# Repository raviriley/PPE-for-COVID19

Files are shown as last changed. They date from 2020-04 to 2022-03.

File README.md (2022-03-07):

Featured on Dr. Neat's Vlog: https://www.youtube.com/watch?v=sHTiJ7Pke1Q

---

##### PPE Makers/Assemblers: [Ravi Riley](https://github.com/raviriley), [Sako Chekerjian](https://github.com/sakorocco), Eric Limonadi, [Adam Komjathy](https://github.com/adamkomjathy)

##### Donors: [FRC Team 589](https://cvrobots.com), my parents, [Dr. Neat](http://www.drneato.com)

##### Recipients: Verdugo Hills Hosptial, Keck Medicine of USC, CVHS, local essential workers

 

---

We need help fabricating face shields and surgical mask strain relievers.

### **Take Action**

Each face shield consists of just 2 parts: a 3D-printed frame and a transparent visor. For more info on the design, click [here](https://3dverkstan.se/protective-visor/).

<div>
<a href="https://mk03dverkstanb4pk6hu.kinstacdn.com/wp-content/uploads/2020/04/liggande1.jpg">

</a>
<a href="https://mk03dverkstanb4pk6hu.kinstacdn.com/wp-content/uploads/2020/04/printoh3.jpg">

</a>
</div>

If you have a 3D printer, print [face shield frames (stl)](https://github.com/raviriley/PPE-for-COVID19/blob/master/Face%20Shield/Face%20Shield%20Frame.stl) and [surgical mask strain relievers (stl)](/surgical%20mask%20strap%20strain%20relief.stl). Ideally print with PETG, if you can't PLA works just as well.
Read this [print guide](https://3dverkstan.se/protective-visor/protective-visor-print-guide/) for more details.

Printing face shield frames one at a time can be super time consuming, so if you want to 3D print stacks of face shields, check out my stack generator on [Thingiverse Customizer](https://www.thingiverse.com/apps/customizer/run?thing_id=4311414) or run its [OpenSCAD script](https://github.com/raviriley/PPE-for-COVID19/tree/master/Face%20Shield/3D%20Printing%20Stacks/Customizable%20stack%20generator) locally. I built this tool using my [STL to OpenSCAD converter](https://github.com/raviriley/STL-to-OpenSCAD-Converter). Scroll down to see a demo of the stack generator script.

If you have a laser cutter, cut [face shield visors](/Face%20Shield/Templates%20%26%20Laser%20Cutting%20files) from transparent 8.5x11" sheets, such as [this](https://www.amazon.com/CFS-Products-Inches-Binding-Covers/dp/B07SB6ZKBD) or [this](https://www.amazon.com/Fellowes-Binding-Presentation-Covers-52089/dp/B0015ZVXIW/).

If you want to help out, please 
so we can buy more filament and plastic sheets. Thank you to our current donors for their contributions!

---

### COVID-19 Information/Trackers

- [CDC - How to make a cloth face mask](https://www.cdc.gov/coronavirus/2019-ncov/prevent-getting-sick/diy-cloth-face-coverings.html)

- [Johns Hopkins Interactive Map](https://coronavirus.jhu.edu/map.html)

- [Google Mobility Trends](https://www.google.com/covid19/mobility/)

---

**Explore more 3D printable designs at the [National Institutes of Health 3D Print Exchange for COVID-19](https://3dprint.nih.gov/collections/covid-19-response)**

---

#### Demo of Face Shield Stacker OpenSCAD Script

Demo of OpenSCAD Script

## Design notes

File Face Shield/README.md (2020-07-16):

To get started, print out a [`0.5in spacer.stl`](https://github.com/raviriley/PPE-for-COVID19/blob/master/Face%20Shield/0.5in%20spacer.stl) for your holepuncher. If you'll be printing face shield frames one at a time, download [`Face Shield Frame.stl`](https://github.com/raviriley/PPE-for-COVID19/blob/master/Face%20Shield/Face%20Shield%20Frame.stl). If you want to print stacks of face shields, explore the stacks folder or click [here](https://www.thingiverse.com/apps/customizer/run?thing_id=4311414) to generate your own custom stacks on Thingiverse Customizer. If you have OpenSCAD, download [`run locally.zip`](https://github.com/raviriley/PPE-for-COVID19/raw/master/Face%20Shield/3D%20Printing%20Stacks/Customizable%20stack%20generator%20(for%20single%20extrusion)/run%20locally.zip) to generate your own custom stacks locally. I suggest rendering locally, as it'll be a lot faster than using Thingiverse Customizer since these are quite large files. 
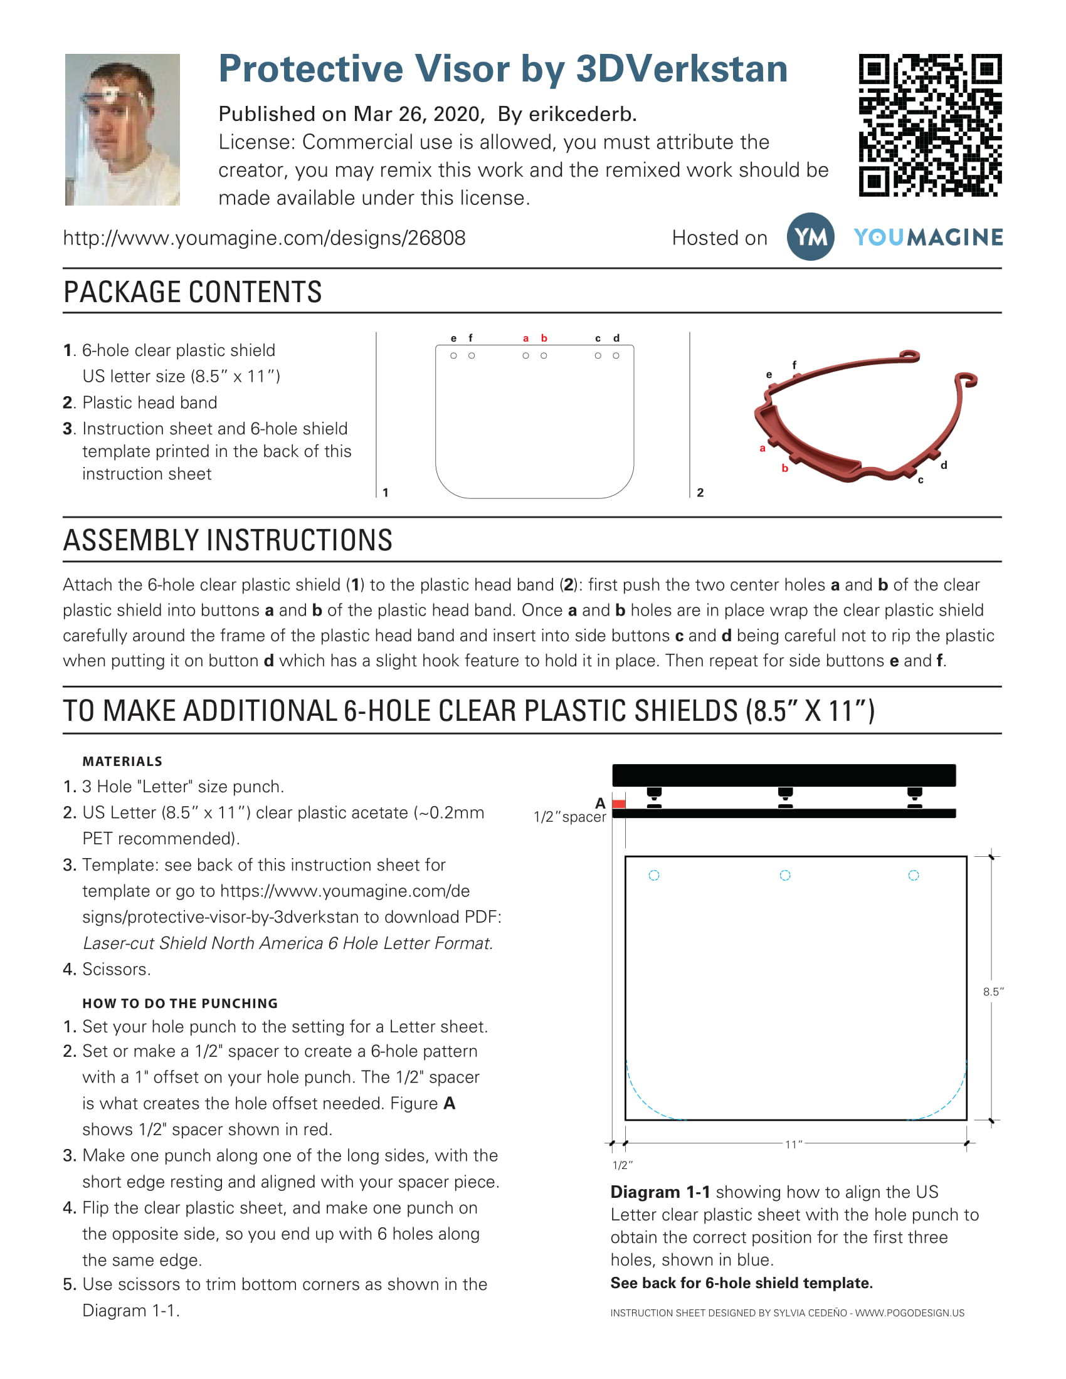
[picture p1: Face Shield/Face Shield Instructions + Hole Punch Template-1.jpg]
Face Shield Instructions and Hole Punch Template Page 1

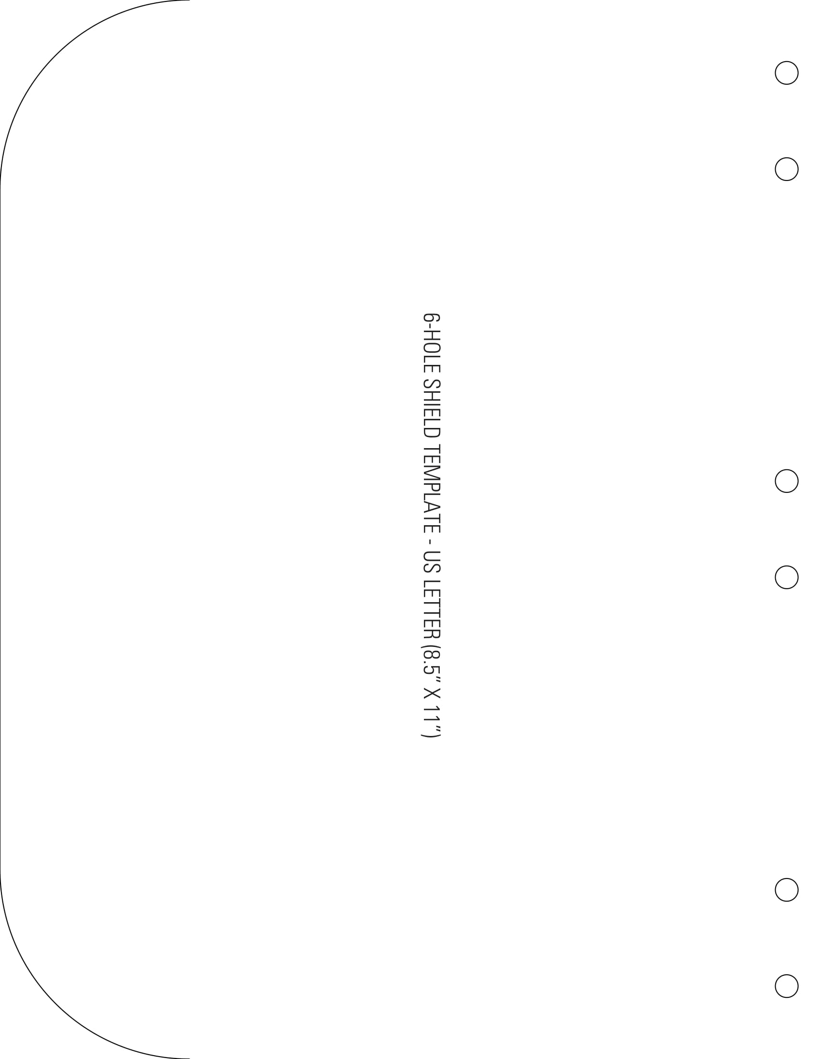
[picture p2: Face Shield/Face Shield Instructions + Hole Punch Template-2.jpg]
Face Shield Instructions and Hole Punch Template Page 2


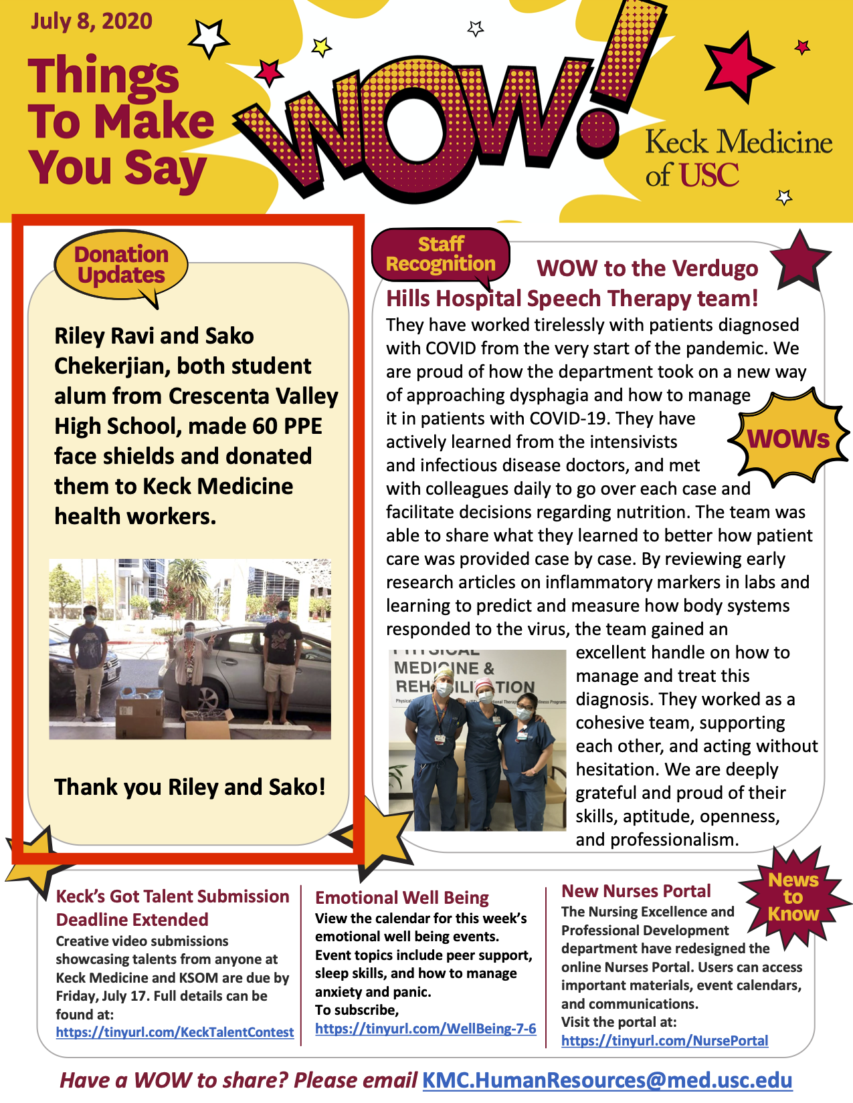
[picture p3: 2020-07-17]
images/USC-newsletter.png

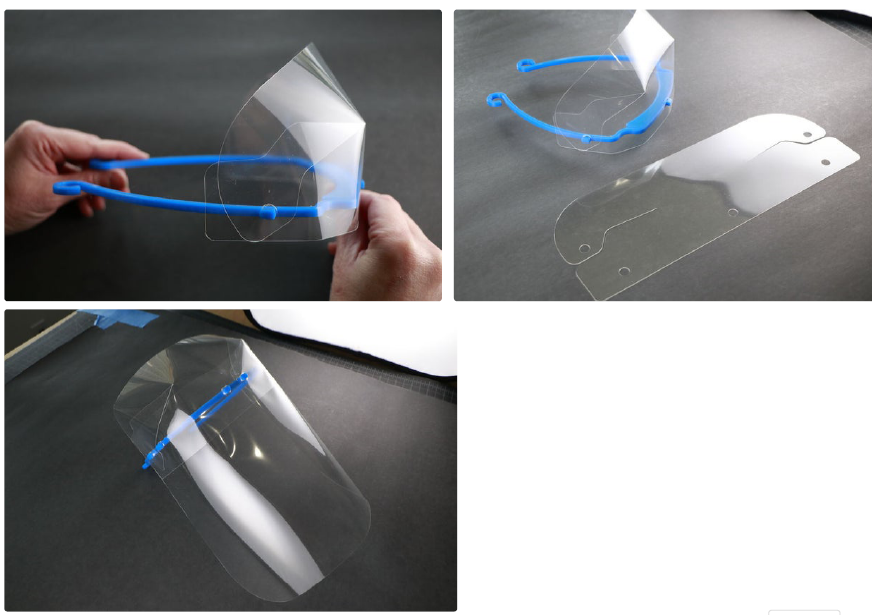
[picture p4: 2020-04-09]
Face Shield/Templates & Laser Cutting files/Top Covers/Capture.PNG

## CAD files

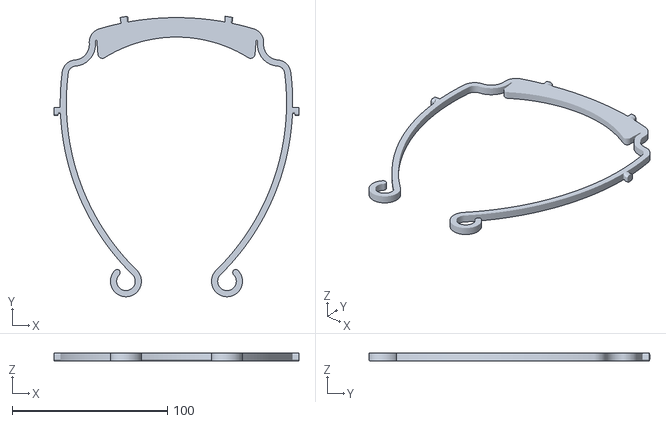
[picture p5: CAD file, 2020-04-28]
Face Shield/3D Printing Stacks/Customizable stack generator/Europe ISO838_v4-solid_front.stl
158.0 x 181.0 x 5.00

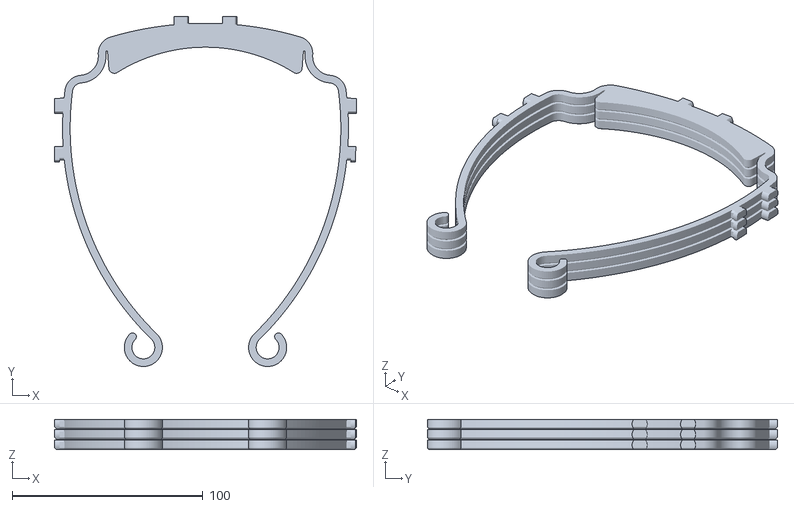
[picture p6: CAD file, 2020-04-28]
Face Shield/3D Printing Stacks/stack of 3 - 16mm tall.stl
158.5 x 183.6 x 16.0

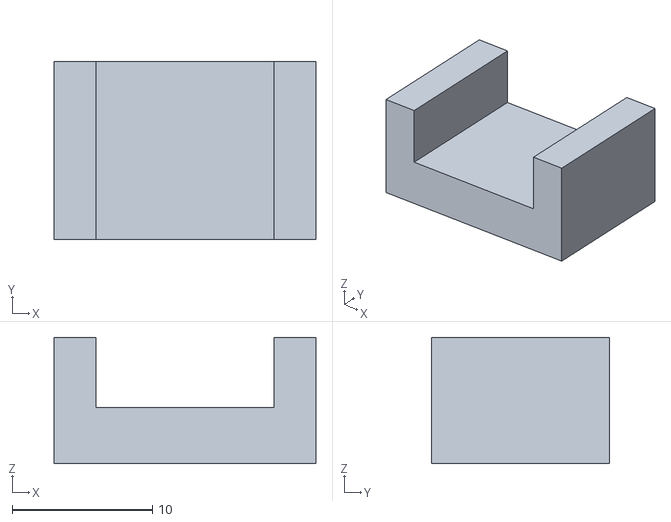
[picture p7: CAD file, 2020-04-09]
Face Shield/all US frame variants/Letter-spacer-6hole.stl
18.7 x 12.7 x 9.00

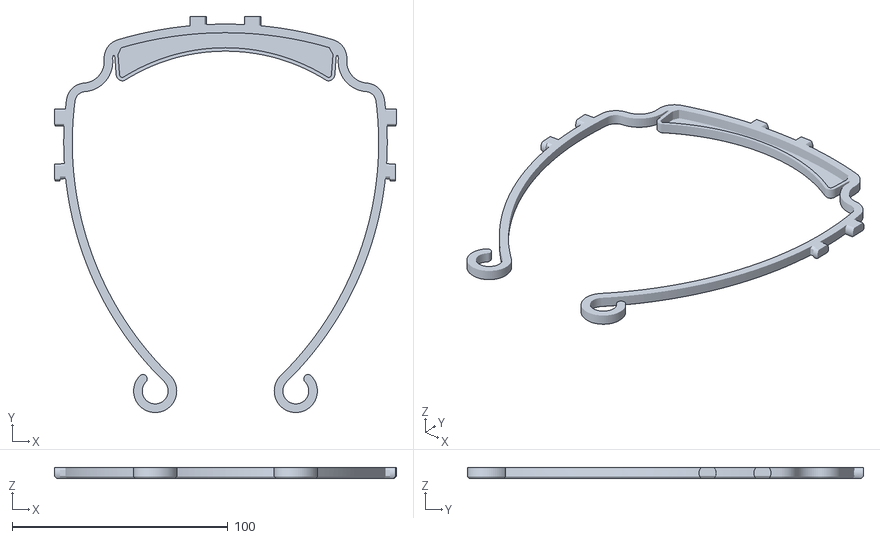
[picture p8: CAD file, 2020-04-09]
Face Shield/Face Shield Frame.stl
158.5 x 183.6 x 5.00

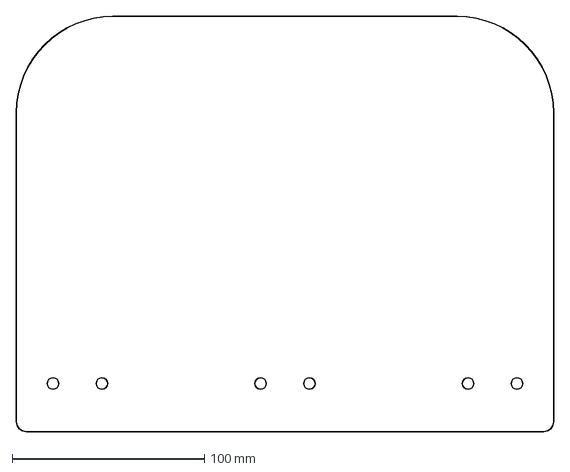
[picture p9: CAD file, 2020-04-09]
Face Shield/Templates & Laser Cutting files/US 6 Hole Template by Joel Telling.dxf
279.4 x 215.9 mm

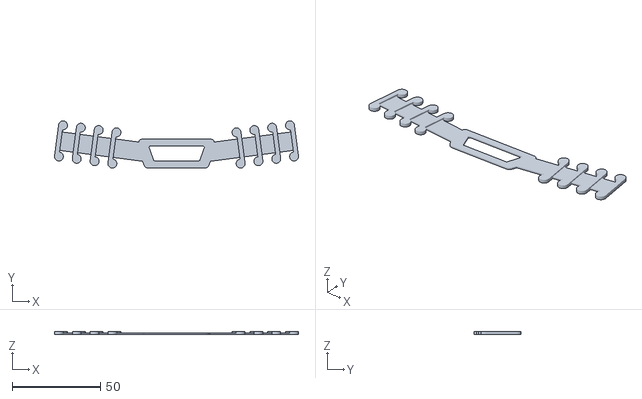
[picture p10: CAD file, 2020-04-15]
surgical mask strap strain relief.stl
138.5 x 26.8 x 1.70

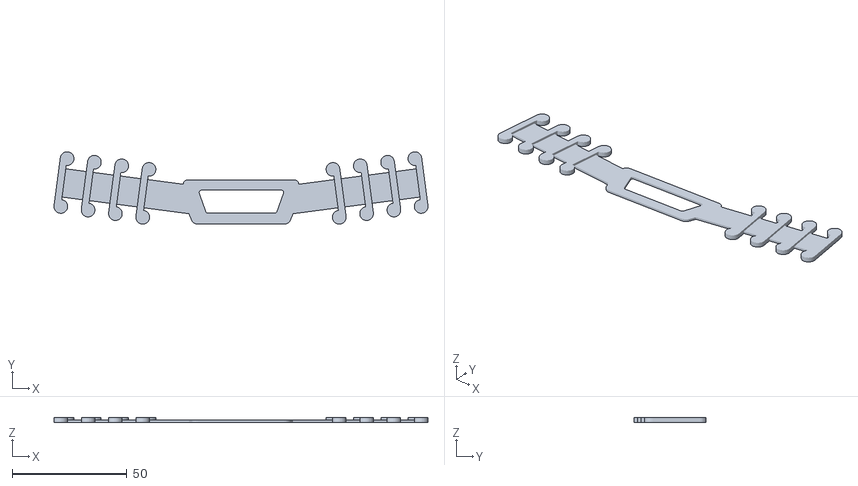
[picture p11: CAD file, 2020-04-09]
Surgical mask strap strain relief large.stl
163.0 x 31.5 x 2.00

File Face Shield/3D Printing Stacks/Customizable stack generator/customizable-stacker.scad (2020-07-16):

/*
3D Verkstan Face Shield Stacker

    This script generates a vertical stack of face shield frames, which enables many frames to be printed at once. You can either max out your build volume or choose the number of frames you want in the stack.
    
Created by Ravi Riley
*/

//Choose North American, Swedish, European, or the Prusa visor compatible variant of the face shield
Variant = "North America"; //[North America, Sweden, Europe, Prusa Compatible]
//(mm)
Build_volume_height = 200;
//(mm)
Layer_height = 0.25;

//Generate max number of frames that can fit in the entered build volume or a user specified amount
Number_of_face_shield_frames_in_a_stack = "User Specified"; //[User Specified, Maximum]

//Number of face shield frames (ignore if you chose maximum above)
User_Specified = 1;

//Number of layers between each face shield frame
Layer_gap = 2; 
/*
    With a 0.4mm nozzle, a 0.25mm layer height works great with a 2 layer gap on my printer. If you are printing with a larger layer height, I suggest decreasing the layer gap to 1 layer.
*/

/* [Hidden] */
unit_height = (5+(Layer_gap*Layer_height)); //5mm = height of each face shield frame
echo ("Unit Height:");
echo (unit_height);

max_frames = floor(Build_volume_height/unit_height); //max number of face shield frames that can fit in the entered build volume
echo ("Max frames:");
echo (max_frames);

if (Number_of_face_shield_frames_in_a_stack == "User Specified") {
    current_height = (User_Specified*unit_height-0.5);
    echo ("Current height:");
    echo (current_height);
}
else {
    current_height = (max_frames*unit_height-0.5);
    echo ("Current height:");
    echo (current_height);
}

/// end customizable parameters ///
//include <utils/build_plate.scad>; //for Thingiverse Customizer

module frame() {
    if (Variant == "North America") import("North America 6hole_v5 solid front.stl", convexity=10);
    else if (Variant == "Sweden") import("Sweden_v11-solid_front.stl", convexity=10);
    else if (Variant == "Europe") import("Europe ISO838_v4-solid_front.stl", convexity=10);
    else import("Prusa Compatible solid-front.stl", convexity=10);
}

module stacker(num) {
   for (i = [0 : num-1])
       translate([ 0, 0, unit_height*i ]) children(0);
}

module stack(num) { stacker(num){frame();} }

module maxStack() stack(max_frames);

if (Number_of_face_shield_frames_in_a_stack == "Maximum") maxStack(); else stack(User_Specified);

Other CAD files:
Face Shield/3D Printing Stacks/Customizable stack generator/Sweden_v11-solid_front.stl
Face Shield/all US frame variants/US letter 6-hole v5-1mm front.stl
Face Shield/3D Printing Stacks/Customizable stack generator/Prusa Compatible solid-front.stl
Face Shield/3D Printing Stacks/Customizable stack generator/North America 6hole_v5 solid front.stl
Face Shield/3D Printing Stacks/Customizable stack generator/Thingiverse Customizer version/customizable-stacker with STL modules.scad
Face Shield/3D Printing Stacks/Customizable stack generator/Thingiverse Customizer version/stl2scad conversions/europe.SCAD
Face Shield/3D Printing Stacks/Customizable stack generator/Thingiverse Customizer version/stl2scad conversions/north america.SCAD
Face Shield/3D Printing Stacks/Customizable stack generator/Thingiverse Customizer version/stl2scad conversions/prusa.SCAD
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

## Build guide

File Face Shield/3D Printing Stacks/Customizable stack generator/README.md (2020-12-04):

Demo of OpenSCAD Script

#### [Thingiverse Customizer Link](https://www.thingiverse.com/apps/customizer/run?thing_id=4311414)

I created a customizable OpenSCAD script that allows you to easily pick the face shield variant you need and build vertical stacks to mass-produce them. If you have OpenSCAD and want to run this locally, download [`run locally.zip`](https://github.com/raviriley/PPE-for-COVID19/raw/master/Face%20Shield/3D%20Printing%20Stacks/Customizable%20stack%20generator%20(for%20single%20extrusion)/run%20locally.zip). This will be much faster than rendering in Thingiverse Customizer. 

### Features
- Number of parts in a stack - either specify a number yourself or let the script calculate the max number of face shields that will fit in your build volume.
- Variant selection - easily choose between one of the four (North America, Europe, Sweden, and Prusa visor compatible)
- Customizable layer height and number of layers of gap between each face shield frame
- Automatic spacing generation between each frame

### Print Settings
No supports!

With a 0.4mm nozzle, a 0.25mm layer height works great with a 2 layer gap on my printer. If you are printing with a larger layer height, I suggest decreasing the layer gap to 1 layer.

In order for the layer gap to work correctly, every layer must be an integer multiple of the layer height. This means the first layer MUST BE 100% of the layer height, or 200%, 300%, etc. 

### How I Designed This
Thingiverse Customizer doesn't support the `import` command, so I converted each STL into an OpenSCAD module using my [STL to OpenSCAD Converter](https://raviriley.github.io/STL-to-OpenSCAD-Converter/). This results in a massive OpenSCAD file, as they all have to be in one file for Customizer to work. 
Originally, I simply used the `import` command to reference each STL, which results in much faster rendering and stack STL generation. `run locally.zip` contains the original .scad file that uses the `import` command, along with each referenced STL.

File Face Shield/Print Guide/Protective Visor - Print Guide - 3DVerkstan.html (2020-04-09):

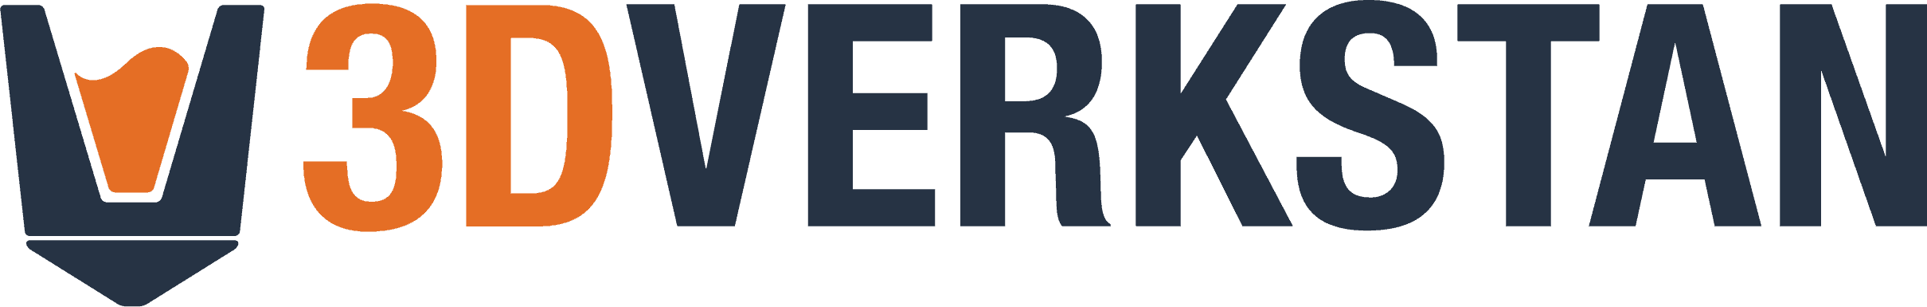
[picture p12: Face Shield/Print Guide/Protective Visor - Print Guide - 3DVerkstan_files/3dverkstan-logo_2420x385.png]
3DVerkstan
 (https://3dverkstan.se/)Meny

# Protective Visor – Print Guide

#3DVFaceShield

< Back to the main article (https://3dverkstan.se/protective-visor/protective-visor/)

This is the guide on how to choose your print settings and print the protective visors / face shields. For best quality we strongly recommend that you follow these settings.

The settings described below is described with the terminology used in Ultimaker Cura,
but they should be possible to enter in any slicer on the market that allows you to change settings.

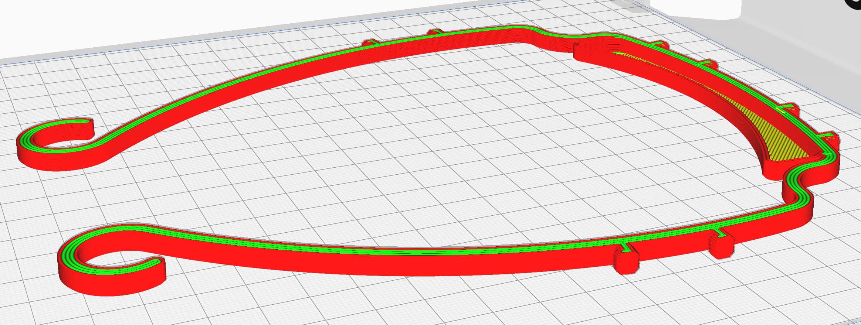
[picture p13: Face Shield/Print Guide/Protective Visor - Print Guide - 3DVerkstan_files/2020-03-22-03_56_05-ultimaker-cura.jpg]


### What filament should i use?

So far, all the most common rigid plastics used in Filament based 3D Printing has shown promise to work well.

If you are buying filament especially for this project, go with PETG or another Co-Polyester, these have better temperature resistance and a slightly better tolerance to some chemicals, but if PLA is all you got, go with it!

The filaments you should NOT be using is:

- Anything flexible, TPU, TPC or similar.
- Anything deliberatly porous, like Polymatte or Colorfabb LW-PLA
- Wood or other natural fiber filled polymers, these can absorb fluids.
- PVB, PVA or BVOH, anything that is easily souluble in either alcohol or water, PolySmooth is not a suitable filament for using to make these since it will dissolve in the desinfection the hospital will use.
- PMMA, since it has very low resistance to alcohols.

We have not evaluated usin resin printers to print face shield frames.

### What SETTINGS should i use?

### What Infill percentage should i use?

This model is made to print with no infill at all. But it is also made to be printed fully solid.

This means that you can set your infill percentage to 0%, as long as you follow the suggested line width and wall number settings below. This will make your print the strongest and fastest to print.

It is important that the print has as few voids as possible, since this will increase the drying time every time it is dipped in disenfectant solution and make it harder to clean.

### What NOZZLE SIZE / LINE WITH should i use?

Since one of the key things in this project is to get the production volume high, if you have the possibility, we suggest you to use a larger than standard nozzle and a larger layer height than you may be used to.

The parts are fully printable with nozzles up to 1.2mm if you choose proper settings, and if you have a high-flow hotend like the Mosquito Magnum or the E3D Supervolcano you should try to use these to your advantage.

What you have to do is to set all your line widths to a multiple of approximately 4mm.

Be aware that Cura hides quite a few of the settings as deafult, so turn the setting visibility to "expert"

Set your number of walls to be equal to ~2.5mm, so with 0.8mm line width you should have at least 3 walls thickness, with 0.4mm it should be at least 5, and with 1.33mm line width only 2 walls is needed.

This means that the optimal line width is:

- 0.4mm nozzle -> Set line width to 0.5mm
- 0.6mm nozzle -> Set line width to 0.66 or 0.8mm
- 0.8 mm nozzle -> Set line width to 0.8mm or 1.0mm
- 1.0mm nozzle -> Set line width to 1.0mm
- 1.2mm nozzle -> Set line width to 1.33mm

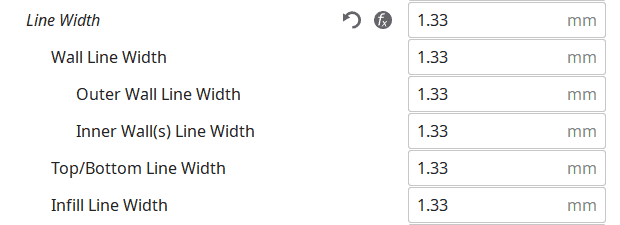
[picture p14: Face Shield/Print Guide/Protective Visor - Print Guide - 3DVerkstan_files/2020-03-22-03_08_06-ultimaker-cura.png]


### What Layer height should i use?

The design is very compatible with thick layers with no negative effects, so the answer is "as thick as possible".

The main limiting factor will be your nozzle size, since the layers need a fair bit of compression, by default it limits you to about 2/3rds or 66% of your nozzle size in mm as layer thickness.

You do need to keep your layer height at 0.6mm or below, or the thin drip protection area above the eyes will fail to print.

The layer heights we suggest to use are:

- 0.4mm: 0.25mm (standard hotend)
- 0.6mm: 0.3mm (standard hotend)
- 0.8mm: 0.3mm (standard hotend)
- 0.8mm: 0.5mm (high-flow hotend)
- 1.0mm: 0.6mm (high-flow hotend)
- 1.2mm: 0.6mm (high-flow hotend)



### What Print speed should i use?

Since this design has no real overhangs and little need for cooling, the main limiting factor for how fast you can push out these frames will be your hotend flow rate.

The hotend flow rate is the number that determines how much plastic your printer can melt in a certain amount of time.

If you just want to start printing:

Start with our suggested layer thickness and line width for the nozzle you are using, and a print speed of at 40mm/sec. This should work on almost any printer.

Make sure to set all the different print speed settings to the same number, this design caters very well to this.

Ultimaker Cura has quite a few "hidden" print speed settings, but if you turn on "expert" mode you can set all of them.

The only one that should be lower is the "initial layer print speed", since it important for bed adhesion. A good starting value is about 20mm/sec.

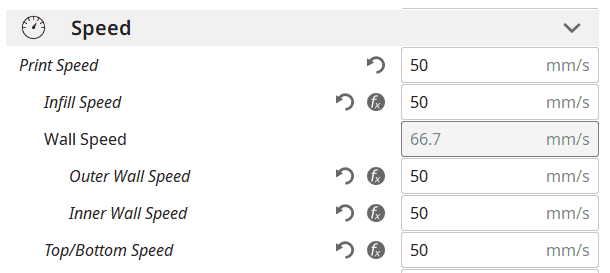
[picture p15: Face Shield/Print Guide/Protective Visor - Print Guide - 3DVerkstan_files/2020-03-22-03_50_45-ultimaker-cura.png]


If you are a advanced user and want to speed up production:

For a regular E3D V6 this is about 10mm3/sec, wich with a 0.8mm nozzle and 0.3mm layer height is calculated as: 10mm^3/(0.8mm*0.3mm) = ~40mm/sec,

A high-flow hotend like the Mosquito magnum with a 0.8mm nozzle and a 1.0mm line width can on the other hand push more than 30mm3/sec, or 30mm^3/(1.0mm*0.5mm)= ~60mm/sec

A super high flow hotend like the E3D Supervolcano can melt up to 100mm3/sec, and with a 1.2mm nozzle and 1.33mm line width it can push 100mm3^3/(1.33mm*0.6mm) = ~125mm/sec

In practice, it might be hard to reach these numbers for other reasons, and if you see signs of your printer underextruding or wanting to grind, start by lowering your print speed by 5mm/sec and increasing your print temperature by 5 degrees.

### What should i look for in the layer preview?

You know that you have a good sliced file when you look at the layer preview and the following is true:

- All lines follows the shape, no zig-zag patterns except on the thin surface in the front.
- No weird break-ups in the lines where it looks like multiple short lines make up a longer one with small spaces in between
- All lines seem to be touching each other, no large spaces in between them.

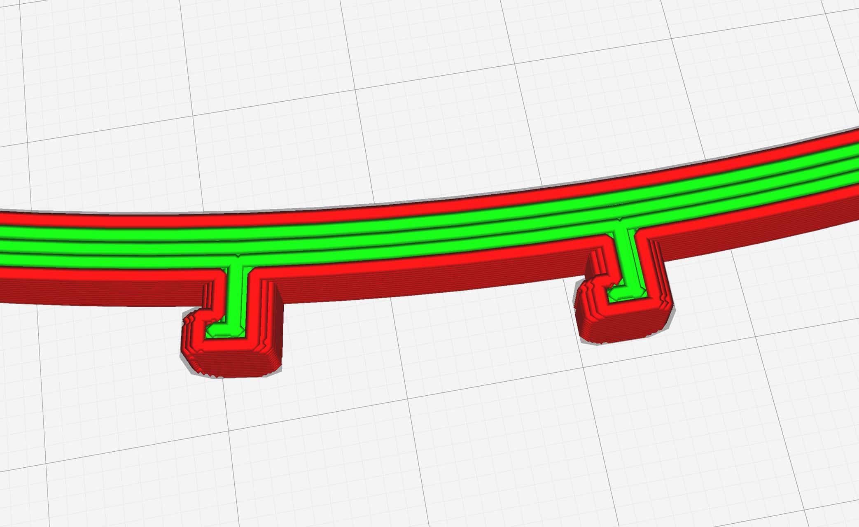
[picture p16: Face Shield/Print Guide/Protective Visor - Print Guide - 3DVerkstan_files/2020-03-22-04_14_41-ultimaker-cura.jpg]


### And now what?

##### Continue to read our articles about the rest of the process:

Choosing the correct version to print & how to punch the holes (https://3dverkstan.se/protective-visor/protective-visor-versions/)

#3DVFaceShield

< Back to the main article (https://3dverkstan.se/protective-visor/protective-visor/)

×

## Dina varor

Du har inga produkter i varukorgen.

Prenumerera på
3DVerkstans nyhetsbrev (https://3dverkstan.us9.list-manage.com/subscribe?u=76409858938be614cc94d2b5b&id=ae6add8dd6)

08-55 11 57 50
info@3dverkstan.se

Rehnsgatan 16 (https://goo.gl/maps/gJCHvyjpxRz3PgbbA)
113 57 Stockholm (https://goo.gl/maps/gJCHvyjpxRz3PgbbA)

 (https://3dverkstan.se/)

- Support (https://3dverkstan.se/support/)
- Blogg (https://3dverkstan.se/nyheter/)
- Integritetspolicy (https://3dverkstan.se/kontakt/integritetspolicy/)
- Köp- och leveransvillkor (https://3dverkstan.se/kop-och-leveransvillkor/)

(https://www.facebook.com/3DVerkstan/) (https://twitter.com/3DVerkstan) (https://www.linkedin.com/company/3dverkstan/) (https://www.instagram.com/3dverkstan/)

Priserna gäller exklusive moms med reservation för ändringar.

© 2019 3DVerkstan AB

×

Du har inga produkter i varukorgen.

Varukorg Artikel borttagen. Ångra (https://3dverkstan.se/protective-visor/protective-visor-print-guide/#0)

- Inga artiklar i varukorgen.

Till kassan - 0 kr (https://3dverkstan.se/checkout/) (https://3dverkstan.se/protective-visor/protective-visor-print-guide/#)

- 0
- 1

Vi använder cookies för att se till att vi ger dig den bästa upplevelsen på vår hemsida. Om du fortsätter att använda den här webbplatsen kommer vi att anta att du godkänner detta.Ok (https://3dverkstan.se/protective-visor/protective-visor-print-guide/#)Nej (https://3dverkstan.se/protective-visor/protective-visor-print-guide/#)Integritetspolicy (https://3dverkstan.se/om-oss/integritetspolicy/)

Ok (https://3dverkstan.se/protective-visor/protective-visor-print-guide/#)

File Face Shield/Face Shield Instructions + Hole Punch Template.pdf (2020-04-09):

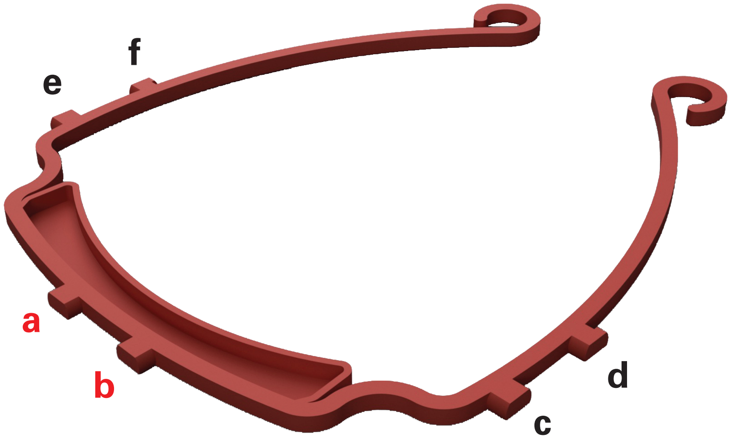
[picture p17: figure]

Attach the 6-hole clear plastic shield (1) to the plastic head band (2): first push the two center holes a and b of the clear plastic shield into buttons a and b of the plastic head band. Once a and b holes are in place wrap the clear plastic shield carefully around the frame of the plastic head band and insert into side buttons c and d being careful not to rip the plastic when putting it on button d which has a slight hook feature to hold it in place. Then repeat for side buttons e and f.

MATERIALS
1. 3 Hole "Letter" size punch.
2. US Letter (8.5” x 11”) clear plastic acetate (~0.2mm PET recommended).
3. Template: see back of this instruction sheet for template or go to https://www.youmagine.com/designs/protective-visor-by-3dverkstan to download PDF: Laser-cut Shield North America 6 Hole Letter Format.
4. Scissors.

HOW TO DO THE PUNCHING
1. Set your hole punch to the setting for a Letter sheet.
2. Set or make a 1/2" spacer to create a 6-hole pattern with a 1" offset on your hole punch. The 1/2" spacer is what creates the hole offset needed. Figure A shows 1/2" spacer shown in red.
3. Make one punch along one of the long sides, with the short edge resting and aligned with your spacer piece.
4. Flip the clear plastic sheet, and make one punch on the opposite side, so you end up with 6 holes along the same edge.
5. Use scissors to trim bottom corners as shown in the Diagram 1-1.

# Protective Visor by 3DVerkstan

Published on Mar 26, 2020, By erikcederb.

### License: Commercial use is allowed, you must attribute the creator, you may remix this work and the remixed work should be

made available under this license.
http://www.youmagine.com/designs/26808 | Hosted on

# PACKAGE CONTENTS

1. 6-hole clear plastic shield
US letter size (8.5” x 11”)

### 2. Plastic head band 3. Instruction sheet and 6-hole shield

template printed in the back of this instruction sheet

# ASSEMBLY INSTRUCTIONS

# TO MAKE ADDITIONAL 6-HOLE CLEAR PLASTIC SHIELDS (8.5” X 11”)

1 2

e f | a b | c d

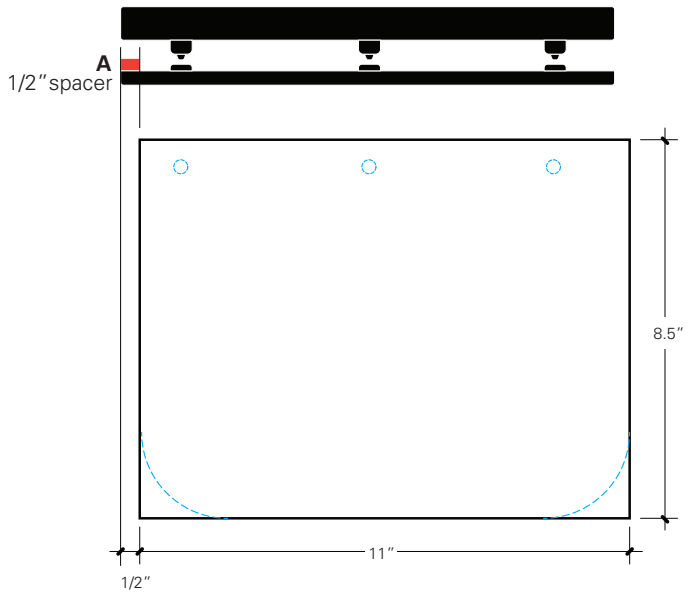
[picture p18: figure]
A 1/2”spacer

Diagram 1-1 showing how to align the US Letter clear plastic sheet with the hole punch to obtain the correct position for the first three holes, shown in blue.
See back for 6-hole shield template.

INSTRUCTION SHEET DESIGNED BY SYLVIA CEDEÑO - WWW.POGODESIGN.US

## 6-HOLE SHIELD TEMPLATE - US LETTER (8.5” X 11”)

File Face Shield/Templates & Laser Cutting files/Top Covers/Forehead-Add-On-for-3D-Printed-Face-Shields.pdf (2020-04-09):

instructables

Forehead Add-On for 3D Printed Face Shields (http://www.instructables.com/id/Forehead-Add-On-for-3D-Printed-Face-Shields/)

by sophywong (http://www.instructables.com/member/sophywong/)

This add-on for 3D printed face shields is cut from plastic transparency sheet and attaches to the pegs of the visor frame over the full sized plastic sheet, extending coverage upwards over the forehead. Quick and easy to make, works with already 3D printed parts.

Light weight, does not block light.
2 add-ons can be cut from 1 sheet of letter size plastic transparency.
Cut with laser cutter, vinyl cutter, or by hand.
Shown with 3D Verkstan’s FaceShield (https://3dverkstan.se/protective-visor/) design, but also compatible with other face shield designs using 6-hole and 3-hole peg con*gurations.

*NOTE: This add-on is an independent project by me, I am not a medical professional, and this add-on has not been tested or approved by anyone. It’s just an idea I had, and I’m sharing it here in case it’s helpful or useful to anyone. If it is useful to you, please let me know!

There are many great designs for 3D printed face shields making the rounds, and one of my favorites is the lightweight and quick-to-print model from 3DVerkstan (https://3dverkstan.se/protective-visor/) in Sweden. The frame of the shield is 3D printed, then a plastic transparency sheet is punched with a standard hole punch, and attached to the pegs of the frame. This design is being printed and used in hospitals *ghting the COVID-19 pandemic around the world. However, some other designs incorporate more coverage at the top of the shield, to provide more protection from aerosolized droplets from above. 3D printed solutions for added upper face coverage result in heavier face shields with signi*cantly increased print times. I wondered if there was a way to incorporate this additional protection into the 3DVerkstan model while still keeping it quick and easy to make.

My design solution is to add another half sheet of transparency plastic to the top, using the same holes and pegs that already exist in the design. This results in no added print time, and the add-on can be attached to existing face shields that have already been printed. I designed this add-on to use half a sheet of transparency plastic, so that 2 add-ons can be cut from 1 sheet of plastic. The add-on snaps onto the frame’s pegs over the full sheet, extending upward, then its side tabs are pulled down and snapped onto the outermost pegs, creating a domed upper shield.

The design cuts in less than a minute on a vinyl or laser cutter. It can also be cut by hand by printing the included *les and using as a cutting pattern, or eyeballed (instructions follow).

Forehead Add-On for 3D Printed Face Shields: Page 1

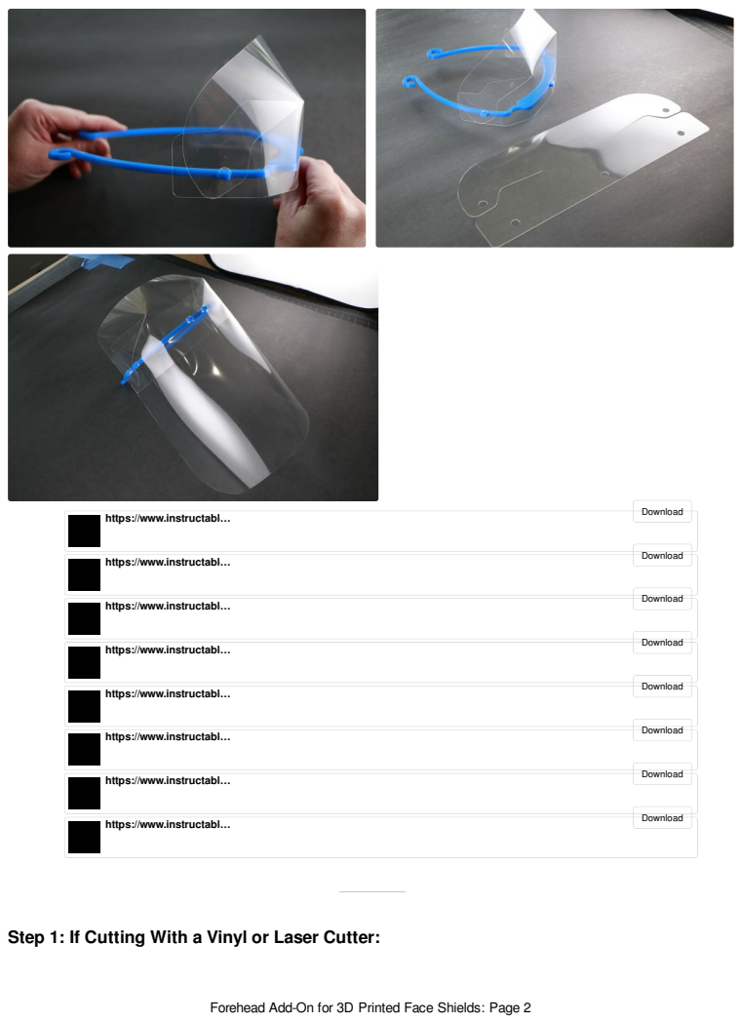
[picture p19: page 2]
Download

https://www.instructabl…

Step 1: If Cutting With a Vinyl or Laser Cutter:

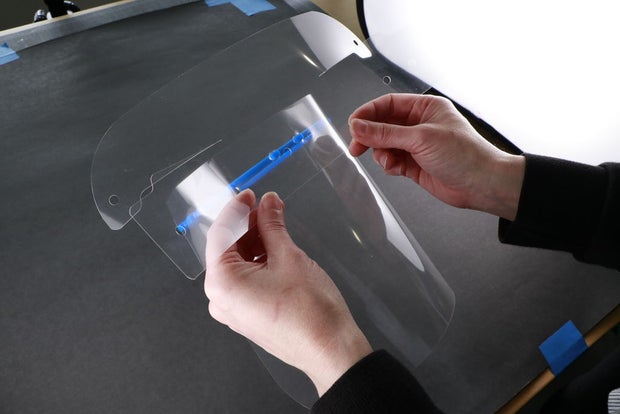
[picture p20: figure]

### Step 2: If Cutting by Hand

Use the appropriate *le for your 3D printed frame (3-hole or 6-hole format) and cut from 8.5" x 11" transparency sheet. Two add-ons will *t on one sheet, so I have provided 2-up *les as well. Once cut, attach to 3D printed frame pegs over the full sized sheet, extending upwards. Then pull outer tabs downward and attach onto outermost pegs on each side of frame, creating the domed structure.

Cut a transparency sheet in half on the long axis to make 2 rectangles 4.25” x 11” each. Each rectangle makes one add-on. Use a 3-hole punch to make holes along one 11” edge, matching the hole spacing for your 3D printed frame (3-hole or 6-hole). Refer to the instructions for your frame design for spacing information. This punched edge is the bottom of your add-on. Use scissors to make a cut at the two bottom

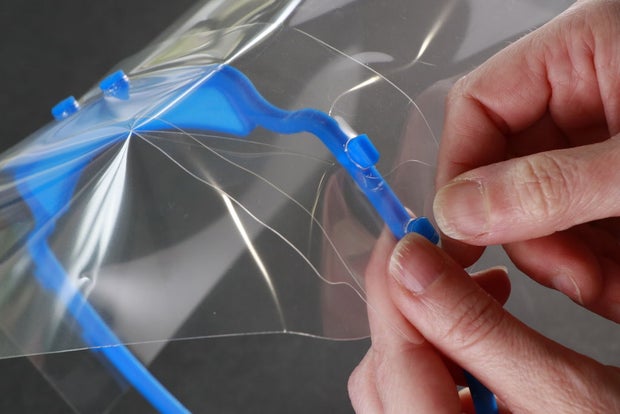
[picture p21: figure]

corners of the add-on, as shown (or refer to pattern). On one side, slide the top section down to the bottom corner, overlapping the punched hole. Mark the location of the hole and punch. Repeat for both sides. Attach add-on to face shield frame over the full sized plastic sheet covering the face. Use scissors to trim any protruding sharp corners.

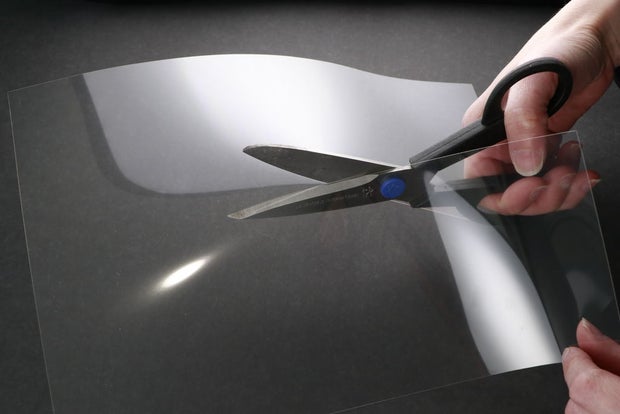
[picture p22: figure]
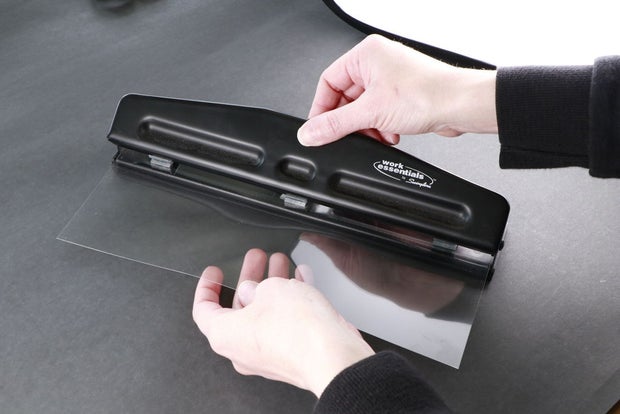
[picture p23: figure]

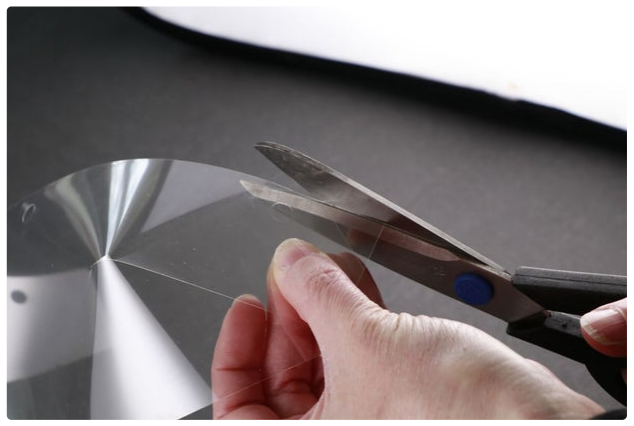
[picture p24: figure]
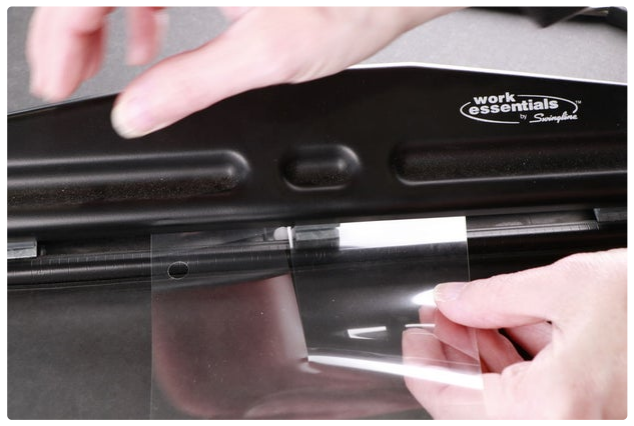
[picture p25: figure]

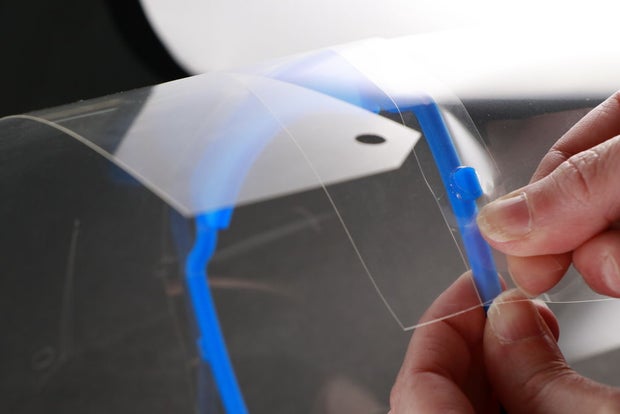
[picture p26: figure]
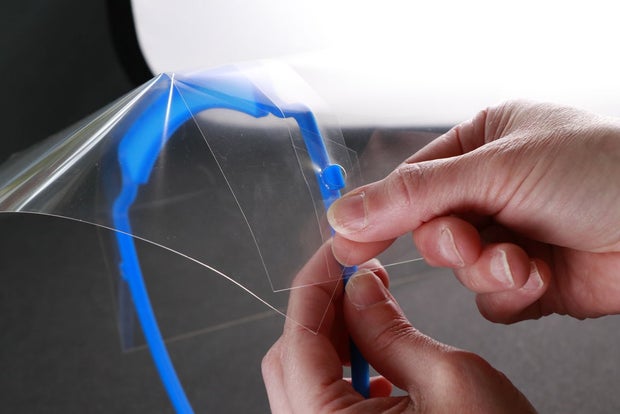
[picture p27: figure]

https://www.instructabl…

Download (https://content.instructables.com/ORIG/FH7/B2XV/K8LRQ9JI/FH7B2XVK8LRQ9JI.pdf)

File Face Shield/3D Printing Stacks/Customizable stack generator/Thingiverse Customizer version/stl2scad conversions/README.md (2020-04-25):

STL to OpenSCAD Converter
http://jsfiddle.net/roha/353r2k8w/embedded/result/

From:
https://www.thingiverse.com/thing:1383325

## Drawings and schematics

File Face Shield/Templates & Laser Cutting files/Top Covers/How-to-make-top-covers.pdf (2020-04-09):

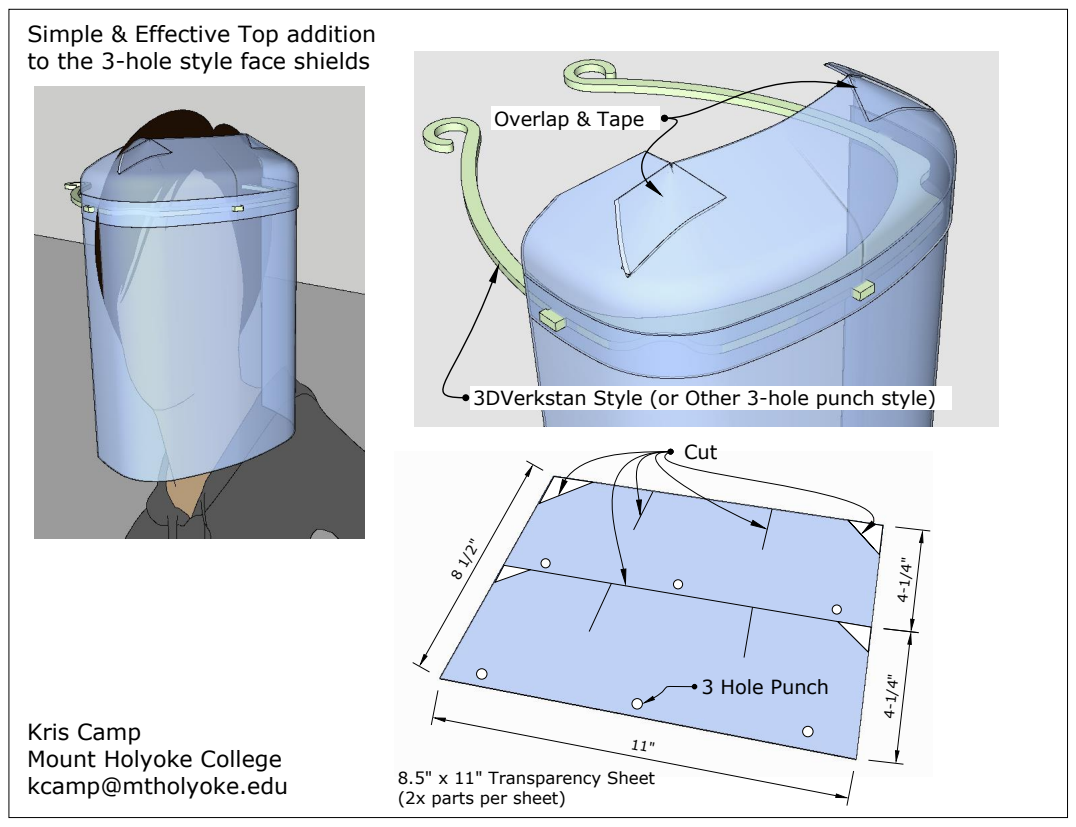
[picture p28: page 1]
Overlap & Tape; 3 Hole Punch

Simple & Effective Top addition
to the 3-hole style face shields

3DVerkstan Style (or Other 3-hole punch style)

Kris Camp
Mount Holyoke College
kcamp@mtholyoke.edu

8.5" x 11" Transparency Sheet
(2x parts per sheet)

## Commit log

2020-04-08 Add prusa face shield folder
    [covid19_chin_rc1us_1pc.stl, covid19_headband_rc3us_1pc.stl, covid19_headband_rc3us_2pcs.stl, covid19_headband_rc3us_4pcs.stl]
2020-04-09 Create Surgical Mask strap strain relief.stl
    [Surgical Mask strap strain relief.stl]
2020-04-09 Face Shields folder
    [Letter-spacer-6hole.stl, US 6 Hole Template by Joel Telling.dxf, Visor Frame PRUSA COMPATIBLE v1.stl, Visor_Frame_NORTH_AMERICA_letter_6-hole_v5-1mm_front.stl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]
2020-04-13 rename strain reliever
    [surgical mask strap strain relief.stl.stl]
2020-04-15 remove extra .stl
    [surgical mask strap strain relief.stl]
2020-04-15 Reorganize folders
    [Letter-spacer-6hole.stl, US 6 Hole Template by Joel Telling.dxf, Visor Frame PRUSA COMPATIBLE v1.stl, Visor_Frame_NORTH_AMERICA_letter_6-hole_v5-1mm_front.stl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]
2020-04-15 update gitignore
    [Visor Frame PRUSA COMPATIBLE v1.stl, Visor_Frame_PRUSA_COMPATIBLE_1mm-front.stl, Visor_Frame_PRUSA_COMPATIBLE_solid-front.stl]
2020-04-15 Changed folders
    [Letter-spacer-6hole.stl, US 6 Hole Template by Joel Telling.dxf, Visor_Frame_NORTH_AMERICA_letter_6-hole_v5-1mm_front.stl, Visor_Frame_NORTH_AMERICA_letter_6-h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]
2020-04-15 rename Print Guide
2020-04-15 Added large version of strain reliever for larger hairdos
    [Surgical mask strap strain relief large.stl, surgical mask strap strain relief.stl]
2020-04-24 Upload stacker supporting files
    [Europe ISO838_v4.stl, North America 6hole_v5.stl, Prusa Compatible.stl, Sweden_v11.stl]
2020-04-24 Create customizable-stacker.scad
    Generates a vertical stack of face shield frames, enabling many 3D prints at once!
    [customizable-stacker.scad]
2020-04-25 Moved STLs to STL folder
    [Europe ISO838_v4.stl, North America 6hole_v5.stl, Prusa Compatible.stl, Sweden_v11.stl]
2020-04-25 Create Europe ISO838_v4.SCAD
    [Europe ISO838_v4.SCAD]
2020-04-25 Create North America 6hole_v5.SCAD
    [North America 6hole_v5.SCAD]
2020-04-25 Create Prusa Compatible.SCAD
    [Prusa Compatible.SCAD]
2020-04-25 Move STLs back to source
    [Europe ISO838_v4.stl, North America 6hole_v5.stl, Prusa Compatible.stl, Sweden_v11.stl]
2020-04-25 Move converted STL to SCAD into Thingiverse Customizer folder
    [Europe ISO838_v4.SCAD, North America 6hole_v5.SCAD, Prusa Compatible.SCAD, Sweden_v11.SCAD]
2020-04-25 Create customizable-stacker - STLs embedded.scad
    [customizable-stacker - STLs embedded.scad]
2020-04-26 Create stack of 32 - 176mm tall.stl
2020-04-28 Create thicker brow stack of 32 - 175.5mm tall.stl
    fixed bridging errors
2020-04-28 Added solid variant of the 6-hole design
    [North America 6hole_v5 solid front.stl]
2020-04-28 Move top covers into laser cutting/templates folder
2020-04-28 Simplified file structure
    [Europe ISO838_v4.SCAD, Europe ISO838_v4.stl, NORTH AMERICA letter 6-hole v5-1mm front.stl, NORTH AMERICA letter 6-hole v5-solid front.stl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]
2020-04-28 Replaced each variants with solid-front version on local run
    [Europe ISO838_v4-solid_front.stl, Europe ISO838_v4.stl, North America 6hole_v5.stl, Prusa Compatible solid-front.stl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]
2020-04-28 Rename and rebuild modules
    [Europe ISO838_v4-solid_front.stl, Europe ISO838_v4.SCAD, North America 6hole_v5 solid front.stl, North America 6hole_v5.SCAD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]
2020-04-28 Create north america.SCAD
    [north america.SCAD]
2020-04-28 Create stack of 3 - 16mm tall
    [stack of 3 - 16mm tall.stl]
2020-04-28 Create stack of 18 - 98.5mm tall.stl
2020-04-28 Create stack of 36 - 197.50mm tall.stl
2020-07-16 Renamed folders and files for simplicity
    [Europe ISO838_v4-solid_front.stl, Letter-spacer-6hole.stl, North America 6hole_v5 solid front.stl, Prusa Compatible solid-front.stl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]
2020-07-16 Create stack of 54 - 297mm tall.stl
2020-07-16 Create stack of 54 - 297mm tall.stl.zip
2020-07-16 Reorganized face shield folder
    [0.5in spacer.stl, Face Shield Frame.stl, Letter-spacer-6hole.stl, US letter 6-hole solid front.stl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]
2020-07-16 Update customizable-stacker.scad
    Added current_height to what echos to console
    [customizable-stacker.scad]
2020-09-09 Reorganized files
    [Europe ISO838_v4-solid_front.stl, North America 6hole_v5 solid front.stl, Prusa Compatible solid-front.stl, Sweden_v11-solid_front.stl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]
